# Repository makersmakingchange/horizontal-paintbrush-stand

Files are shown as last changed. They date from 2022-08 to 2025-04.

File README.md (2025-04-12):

#  Horizontal Paintbrush Stand
This is a paintbrush stand designed for use by a Mouth Painter. The Horizontal Paintbrush Stand has a series of spaced horizontal slots to rest the brush during use and enable the painter to switch between brushes independently. The stand has a female 1/4"-20 UNC connection for mounting using commercially available camera mounting equipment.

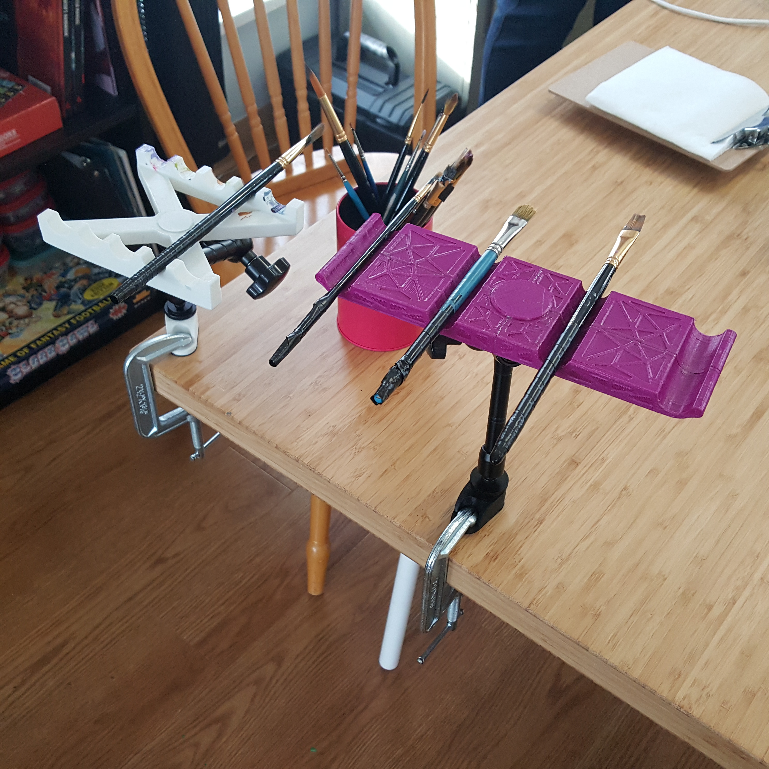
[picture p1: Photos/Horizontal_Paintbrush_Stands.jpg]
Picture of two Horizontal Paintbrush Stands. Each stand is mounted to a table using a Magic Arm, a C-Clamp mounting Adapter, and a C-Clamp.


## More info at
- [Makers Making Change Project Page](https://makersmakingchange.com/project/horizontal-paintbrush-stand/)

## How to Obtain a Horiztonal Horizontal Paintbrush Stand

### 1. Do it Yourself (DIY) or Do it Together (DIT)

This is an open-source assistive technology, so anyone is free to build it. All of the files and instructions required to build the Horizontal Paintbrush Stand are contained within this repository. Refer to the Maker Guide below.

### 2. Request a build of this device

To get matched up with a volunteer maker to build the device, you can submit a build request through the [MMC Library Page](https://makersmakingchange.com/project/horizontal-paintbrush-stand/). As the requestor, you will be responsible for the cost of materials and any shipping.

### 3. How to build this device for someone else

If you have the skills and equipment to build a device like this and would like to donate your time to create the switch for someone who needs it, visit the [MMC Maker Wanted](https://makersmakingchange.com/maker-wanted/) section to get in touch with a user.

## Files
### Documentation
| Document             | Version | Link |
|----------------------|---------|------|
| Design Rationale     | 1.0     | [Horizontal_Paintbrush_Stand_Design_Rationale](/Documentation/Horizontal_Paintbrush_Stand_Design_Rationale_v1.0.pdf)|
| Maker Guide          | 1.0     | [Horizontal_Paintbrush_Stand_Maker_Guide](/Documentation/Horizontal_Paintbrush_Stand_Maker_Guide_v1.0.pdf)          |
| Bill of Materials    | 1.0     | [Horizontal_Paintbrush_Stand_Bill_of_Materials](/Documentation/Horizontal_Paintbrush_Stand_BOM_v1.0.xlsx)           |
| User Guide           | 1.0     | [Horizontal_Paintbrush_Stand_User_Guide](/Documentation/Horizontal_Paintbrush_Stand_User_Guide_v1.0.pdf)            |
| Changelog            | 1.0     | [Horizontal_Paintbrush_Stand_Changelog](/Documentation/Horizontal_Paintbrush_Stand_ChangeLog_v1.0.pdf)              |

### Design Files
[CAD Files](/Design_Files)

### Build Files
 - [3D Printing Files](/Build_Files/3D_Printing)

## Attribution
Designed by Jake McIvor (Makers Making Change) in consultation with artist Kaileen Selig.

## License
Everything needed or used to design, make, test, or prepare the Horizontal Paintbrush Stand is licensed under the CERN 2.0 Permissive license <https://ohwr.org/project/cernohl/wikis/Documents/CERN-OHL-version-2> (CERN-OHL-P) . 

Accompanying material such as instruction manuals, videos, and other copyrightable works that are useful but not necessary to design, make, test, or prepare the Horizontal Paintbrush Stand are published under a Creative Commons Attribution-ShareAlike 4.0 license <https://creativecommons.org/licenses/by-sa/4.0/> (CC BY-SA 4.0).

<!-- ABOUT MMC START -->
## About Makers Making Change
[Makers Making Change Logo](https://www.makersmakingchange.com/)

Makers Making Change is a program of [Neil Squire](https://www.neilsquire.ca/), a Canadian non-profit that uses technology, knowledge, and passion to empower people with disabilities.

Makers Making Change leverages the capacity of community based Makers, Disability Professionals and Volunteers to develop and deliver affordable Open Source Assistive Technologies.

 - Website: [www.MakersMakingChange.com](https://www.makersmakingchange.com/)
 - GitHub: [makersmakingchange](https://github.com/makersmakingchange)
 - Bluesky: [@makersmakingchange.bsky.social](https://bsky.app/profile/makersmakingchange.bsky.social)
 - Instagram: [@makersmakingchange](https://www.instagram.com/makersmakingchange)
 - Facebook: [makersmakechange](https://www.facebook.com/makersmakechange)
 - LinkedIn: [Neil Squire Society](https://www.linkedin.com/company/neil-squire-society/)
 - Thingiverse: [makersmakingchange](https://www.thingiverse.com/makersmakingchange/about)
 - Printables: [MakersMakingChange](https://www.printables.com/@MakersMakingChange)

### Contact Us
For technical questions, to get involved, or to share your experience we encourage you to [visit our website](https://www.makersmakingchange.com/) or [contact us](https://www.makersmakingchange.com/s/contact).
<!-- ABOUT MMC END -->

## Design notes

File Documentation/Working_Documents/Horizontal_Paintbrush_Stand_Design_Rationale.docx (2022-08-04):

# Introduction

This project was originated in consultation with a mouth painter who was looking for a way to independently swap paintbrushes and temporarily but them down to rest. At the time, they were relying on a care aid to initially position the brush so they could grip it in their mouth with their lips and teeth.

# Research

Initial research did not uncover any suitable commercial or pre-existing DIY options. Most commercial options are intended to keep the brush in a vertical position, and do not provide easy access to the handle.

A more recent search did yield a horizontal brush holder (e.g., https://genevafineart.com/collections/all-items/products/brush-holder, $120) but this is expensive and would be difficult to mount at the proper height.

# Requirements

## Goals

G01 | Provide a means for user to independently place down and swap between several paintbrushes.

## Functional Requirements

F01 | The stand must have space for a minimum of 4 brushes.
F02 | The stand must be mounted securely.
F03 | The stand must be easily repositionable to adjust for height.
F04 | The stand must enable user to put down a brush while gripping it with their mouth.
F05 | The stand must enable the user to retrieve a brush by gripping it with their mouth.
F06 | Brushes must be adequately spaced to provide clearance for ventilator.

## Non-functional Requirements

NF01 | Design must be maker-friendly.

## Constraints

C01 | Design must be released open-source.

# Detailed Design

## Brush Slot Spacing

A spacing of 60 mm between the brushes was found to be a good compromise between keeping the brushes close together and allowing enough room between them so they can be easily grasped without interfering with the ventilator. A painter that doesn't use a ventilator may be able to have the brushes spaced closer together.

## Number of Slots

The user requested to have access to at least 3-4 brushes.

## Slot Size

A semi-circular slot with a radius of 8 mm was chosen to accommodate most paint brush handles.

## Mounting

One of the most important functional requirements is that the brush stand is quick and easy to setup and can be adjusted to the right position. A 1/4"-20 UNC tee insert nut was selected as a cost-effective and maker-friendly method of adding a modular mounting connection point. This connection point can be used with a variety of commercially available camera mounting equipment, including an articulating arm, or “Magic Arm”.

The mounting configuration for the user was chosen based on the availability of magic arms from related projects, as well as the requirement to have a non-permanent connection to the working surface.

- 3D printed C-Clamp Adapter (i.e., https://makersmakingchange.com/project/c-clamp-threaded-adapter/)
- Off-the-shelf C-Clamp (e.g., https://www.homedepot.ca/product/bessey-bessey-2-1-2-inch-900-lb-drop-forged-c-clamp-with-1-3-8-inch-throat-depth/1000816966)
- Off-the-shelf Articulating Magic Arm (e.g., https://www.amazon.ca/Koolehaoda-Adjustable-Articulating-Compatible-Microphones/dp/B08PC21P2D)

# V0.1

The initial prototype of the design had five slots, spaced apart by 22 mm. Each slot was a semi-circular with a diameter of 16 mm. The brush is supported by two 10 mm wide sections separated by 90 mm center-to-center.

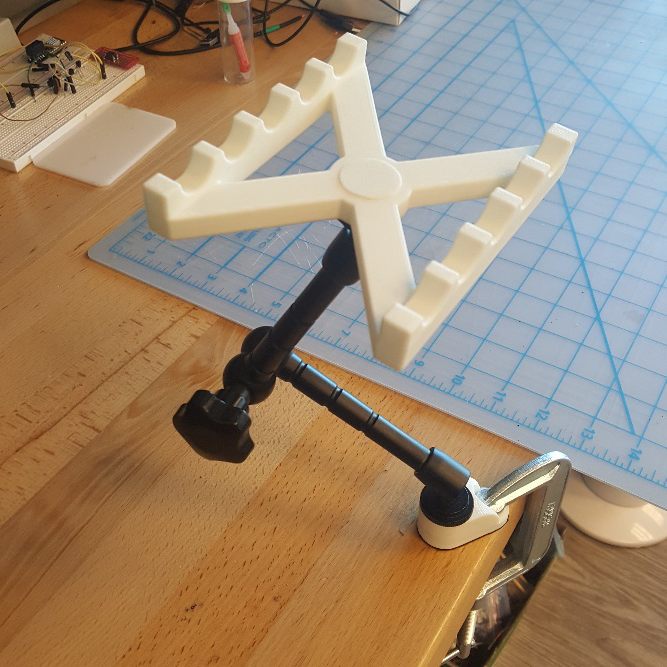
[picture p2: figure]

Figure 1: Initial Prototype

Assembly

The T-Nut is pressed into the stand from the top, and then the cap is glued into place.

# V0.2

Based on feedback from the user, the spacing between brushes was increased from 22 mm to 60 mm and the number of slots was reduced from five to four. Instead of two discrete supports the support was made continuous to make it easier to rest the brushes.

This version was also intended to be more aesthetically stylish.

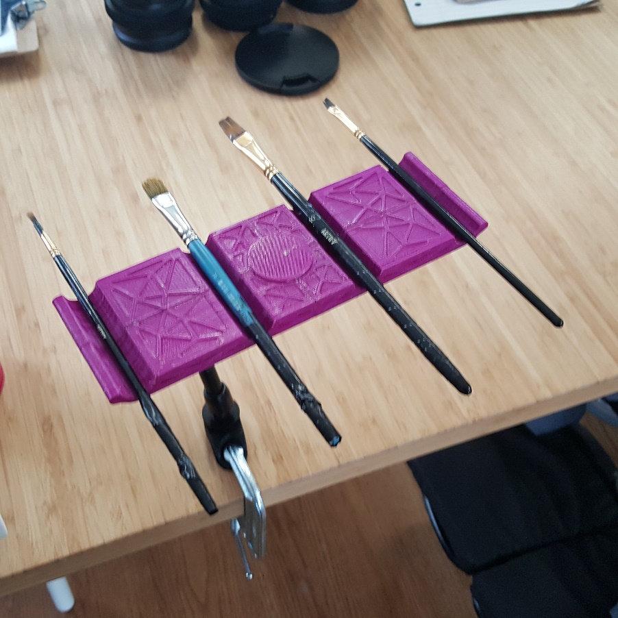
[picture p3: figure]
A picture of a 3d printed horizontal paintbrush stand. This is version 0.2, which features 4 slots.

Figure 2: Version 0.2

© 2022 by Neil Squire. This work is licensed under the CC BY SA 4.0 License: http://creativecommons.org/licenses/by-sa/4.0 Files available at https://makersmakingchange.com/project/horizontal-paintbrush-stand/ Page 1 of 1

V1.0 | JUNE 2022 Horizontal Paintbrush Stand Design Rationale

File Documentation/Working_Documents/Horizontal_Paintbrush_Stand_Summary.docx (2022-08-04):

# Title

Horizontal Paintbrush Stand

## Subtitle

An easily mountable stand for paintbrushes.

## Device Specifications

Build Time:

< 1hr

1-4 hr

5-10hr

>10hr

Cost:

$0 - $10

$11 - $25

$26 - $50

$51 - $100

$101 - $250

$250+

Stage: Recently Added

Skills: 3D Printing; Mechanics

Need: Agility / Dexterity

Disability: Mobility / Physical

Difficulty: Beginner

License: CC BY-SA

Usages: Recreation and Leisure

Type:

Designer: Makers Making Change

## Device Details

### Overview

This is a paintbrush stand designed for use by a Mouth Painter. The Horizontal Paintbrush Stand has a series of spaced horizontal slots to rest the brush during use and enable the painter to switch between brushes independently. The stand has a female 1/4"-20 UNC connection for mounting using commercially available camera mounting equipment.

### Usage

A suitable mounting solution is connected to the bottom of the stand and the working surface. The stand is then positioned at an appropriate height for the user. The user can place and remove brushes to and from the stand as necessary.

### Build Instructions

This build consists of 3D printable parts and some commercial off-the-shelf hardware. Refer to the Maker Guide for instructions on what parts to obtain, and how to print the parts. There are two design variants: A and B.

#### Skills Required

- 3D Printing
- Mechanical Assembly

#### Time Required

3D Printing Time: A: 3h14m / B: 9h45m

Assembly Time: 15 minutes

#### Tools

- ¼”-20 Hex Bolt
- Crescent wrench / pliers for inserting Tee-nut

#### Components

Variant A:

- 1X 3D Printed Base
- 1X 3D Printed Cap
- 1X ¼”-20 UNC Tee Nut

Variant B:

- 2X 3D Printed Base1
- 2X 3D Printed Base2
- 1X 3D Printed Nut Insert
- 1X 3D Printed Cap
- 6X 3D Printed Pins
- 1X ¼”-20 UNC Tee Nut

#### 3D Printing

Refer to the Maker Guide for 3D Printing instructions.

### Design

This device was designed using Autodesk Fusion 360. Original design files are available in the repository.

### Attribution

Designed by Jake McIvor (Makers Making Change) in consultation with Kaileen Selig.

© 2022 by Neil Squire. This work is licensed under the CC BY SA 4.0 License: http://creativecommons.org/licenses/by-sa/4.0 Files available at https://makersmakingchange.com/project/horizontal-paintbrush-stand/ Page 1 of 2

V1.0 | JUNE 2022 Horizontal Paintbrush Stand Summary

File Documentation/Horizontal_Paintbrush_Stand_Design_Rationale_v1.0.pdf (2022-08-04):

V1.0 | JUNE 2022

## Horizontal Paintbrush Stand

## DESIGN RATIONALE

© 2022 by Neil Squire. (https://neilsquire.ca/)
This work is licensed under the CC BY SA 4.0 License: http://creativecommons.org/licenses/by-sa/4.0
Files available at https://makersmakingchange.com/project/horizontal-paintbrush-stand/ | Page 1 of 4

### Introduction

This project was originated in consultation with a mouth painter who was looking for a way to independently swap paintbrushes and temporarily but them down to rest. At the time, they were relying on a care aid to initially position the brush so they could grip it in their mouth with their lips and teeth.

### Research

Initial research did not uncover any suitable commercial or pre-existing DIY options. Most commercial options are intended to keep the brush in a vertical position, and do not provide easy access to the handle.

A more recent search did yield a horizontal brush holder (e.g., https://genevafineart.com/collections/allitems/products/brush-holder, (https://genevafineart.com/collections/all-items/products/brush-holder) $120) but this is expensive and would be difficult to mount at the proper height.

### Requirements

### Goals

G01 Provide a means for user to independently place down and swap between several paintbrushes.

### Functional Requirements

F01 | The stand must have space for a minimum of 4 brushes.
F02 | The stand must be mounted securely.
F03 | The stand must be easily repositionable to adjust for height.
F04 | The stand must enable user to put down a brush while gripping it with their mouth.
F05 | The stand must enable the user to retrieve a brush by gripping it with their mouth.
F06 | Brushes must be adequately spaced to provide clearance for ventilator.

### Non-functional Requirements

NF01 Design must be maker-friendly.

### Constraints

C01 Design must be released open-source.

## DESIGN RATIONALE

Files available at https://makersmakingchange.com/project/horizontal-paintbrush-stand/ | Page 2 of 4

### Detailed Design

### Brush Slot Spacing

A spacing of 60 mm between the brushes was found to be a good compromise between keeping the brushes close together and allowing enough room between them so they can be easily grasped without interfering with the ventilator. A painter that doesn't use a ventilator may be able to have the brushes spaced closer together.

### Number of Slots

The user requested to have access to at least 3-4 brushes.

### Slot Size

A semi-circular slot with a radius of 8 mm was chosen to accommodate most paint brush handles.

### Mounting

One of the most important functional requirements is that the brush stand is quick and easy to setup and can be adjusted to the right position. A 1/4"-20 UNC tee insert nut was selected as a cost-effective and maker-friendly method of adding a modular mounting connection point. This connection point can be used with a variety of commercially available camera mounting equipment, including an articulating arm, or “Magic Arm”.

The mounting configuration for the user was chosen based on the availability of magic arms from related projects, as well as the requirement to have a non-permanent connection to the working surface.

- 3D printed C-Clamp Adapter (i.e., https://makersmakingchange.com/project/c-clamp-threadedadapter/) (https://makersmakingchange.com/project/c-clamp-threaded-adapter/)
- Off-the-shelf C-Clamp (e.g., https://www.homedepot.ca/product/bessey-bessey-2-1-2-inch-900-lbdrop-forged-c-clamp-with-1-3-8-inch-throat-depth/1000816966) (https://www.homedepot.ca/product/bessey-bessey-2-1-2-inch-900-lb-drop-forged-c-clamp-with-1-3-8-inch-throat-depth/1000816966)
- Off-the-shelf Articulating Magic Arm (e.g., https://www.amazon.ca/Koolehaoda-Adjustable-Articulating-Compatible-Microphones/dp/B08PC21P2D) (https://www.amazon.ca/Koolehaoda-Adjustable-Articulating-Compatible-Microphones/dp/B08PC21P2D)

V0.1
The initial prototype of the design had five slots, spaced apart by 22 mm. Each slot was a semi-circular with a diameter of 16 mm. The brush is supported by two 10 mm wide sections separated by 90 mm center-to-center.

## DESIGN RATIONALE

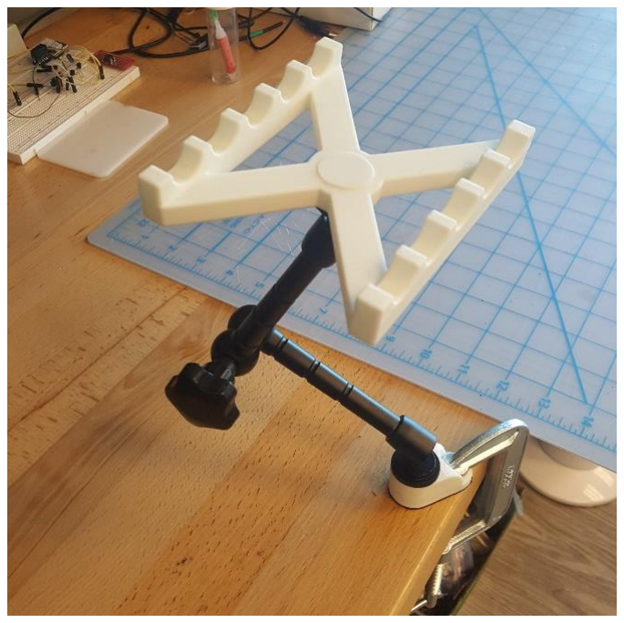
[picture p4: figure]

Files available at https://makersmakingchange.com/project/horizontal-paintbrush-stand/ | Page 3 of 4

Figure 1: Initial Prototype

Assembly

The T-Nut is pressed into the stand from the top, and then the cap is glued into place.

V0.2
Based on feedback from the user, the spacing between brushes was increased from 22 mm to 60 mm and the number of slots was reduced from five to four. Instead of two discrete supports the support was made continuous to make it easier to rest the brushes.

## DESIGN RATIONALE

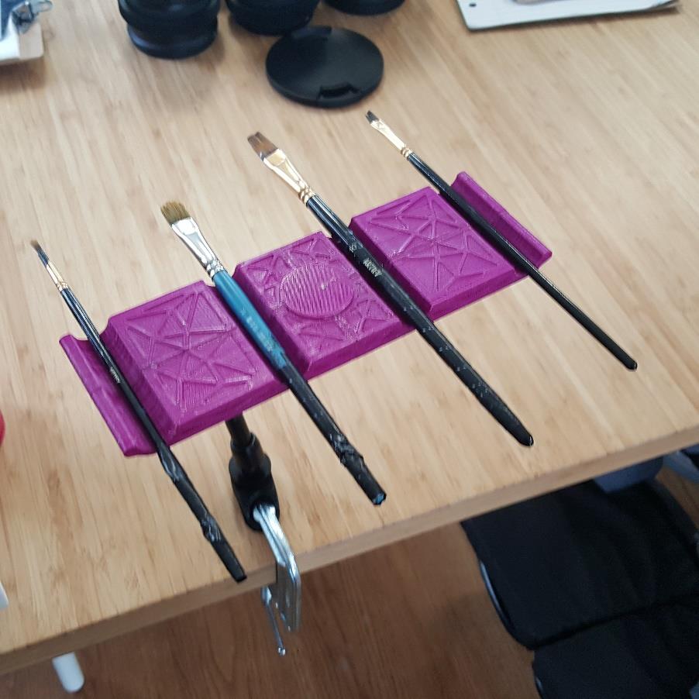
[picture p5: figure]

Files available at https://makersmakingchange.com/project/horizontal-paintbrush-stand/ | Page 4 of 4

This version was also intended to be more aesthetically stylish.

Figure 2: Version 0.2

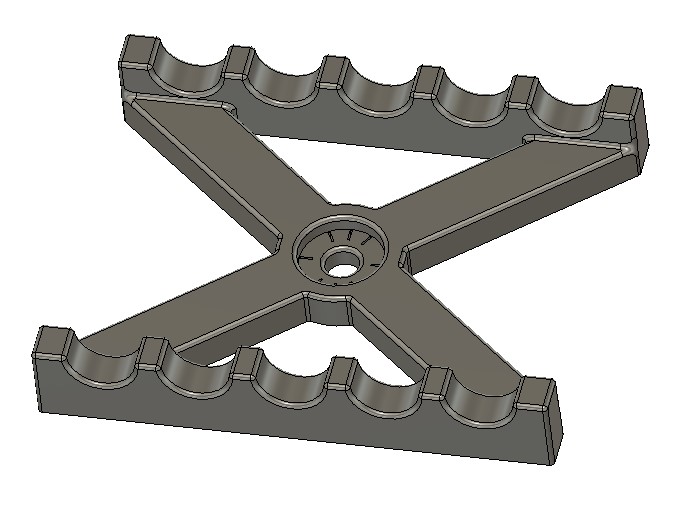
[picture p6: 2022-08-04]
Documentation/Working_Documents/Photos/Initial_Prototype.jpg

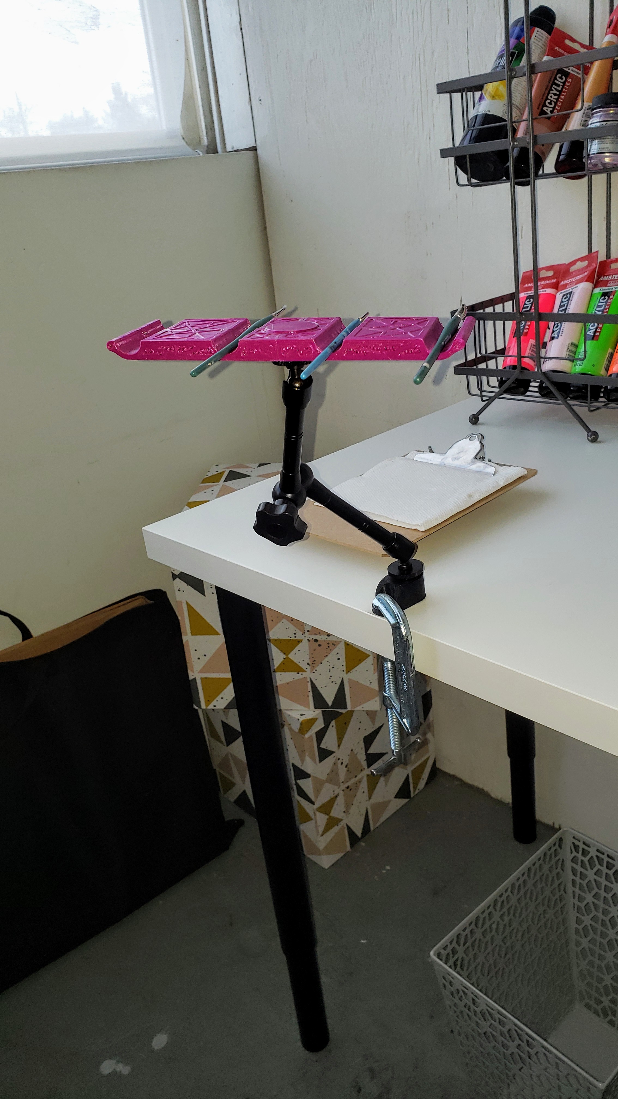
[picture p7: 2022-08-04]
Photos/V0.2/paintbrush stand.jpg

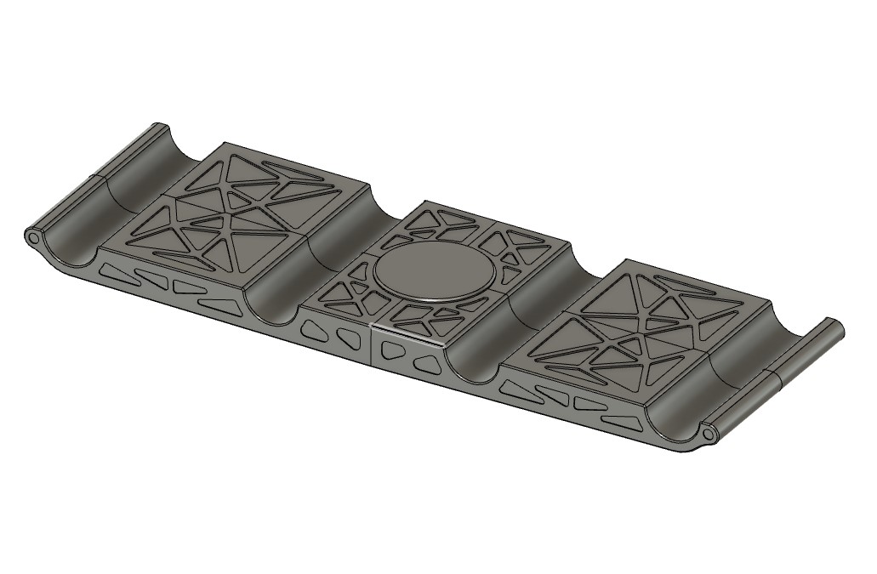
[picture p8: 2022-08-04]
Photos/V0.2/PaintBrushStand_v2.jpg

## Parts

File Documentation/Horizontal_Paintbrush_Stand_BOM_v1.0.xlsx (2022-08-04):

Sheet: BOM-A
Paintbrush Stand |  | Total Cost | Total Print time (hr) | Total filament (g)
Version: Variant A | Last Updated: 2022-Jul-06 | $1.55 | 3.25 | 43
Commercial Parts:
 | Part Name | QTY | Pkg QTY | PKG Price | Price per Unit | Price for qty needed | Link
Mechanical | 1/4"-20 UNC Tee Nut | 1 | 1 | $0.48 | $0.48 | $0.48 | https://www.homedepot.ca/product/paulin-1-4-inch-20-tee-nuts-4-prong-5-16-inch-barrel-length/1000129429
 |  | 0
 |  | 0
3D Printed Parts ESTIMATED PRICING USING 1KG ROLL COST: | $25.00
Part | Description | Quantity Needed | TOTAL Mass (g) | Estimated Price | Print Time (Min) |  | Link
A_Base |  |  | 42 | $1.05 | 192
A_Cap |  |  | 1 | $0.03 | 3
 |  |  |  | $0.00
 |  |  |  | $0.00
 |  |  |  | $0.00
 |  |  | Total Print Cost: | $1.07
Tools for Assembly
1/4"-20 Bolt
Alternatives (if there are other sources for some parts link them below)
Part and description | Link

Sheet: BOM-B
Paintbrush Stand |  | Total Cost | Total Print time (hr) | Total filament (g)
Version: Variant B | Last Updated: 2021-10-30 | #DIV/0! | 9.72 | 88
Commercial Parts:
Part type (Electrical. Mechanical, Sanitization, ect) | Part Name | Quantity Needed | Pkg Quantity | Price per package | Price per Unit | Price for qty needed | Link
Mechanical | 1/4"-20 UNC Tee Nut | 1 | 1 | $0.48 | $0.48 | $0.48 | https://www.homedepot.ca/product/paulin-1-4-inch-20-tee-nuts-4-prong-5-16-inch-barrel-length/1000129429
 |  |  |  |  | #DIV/0! | #DIV/0!
 |  |  |  |  | #DIV/0! | #DIV/0!
3D Printed Parts ESTIMATED PRICING USING 1KG ROLL COST: | $25.00
Part | Description | Quantity Needed | TOTAL Mass (g) | Estimated Price | Print Time (Min) |  | Link
B_Base 1 |  | 2 | 39 | $0.97 | 265
B_Base 2 |  | 2 | 39 | $0.97 | 265
B_Nut Insert |  | 1 | 6 | $0.15 | 35
B_Cap |  | 1 | 2 | $0.05 | 9
B_Pin |  | 6 | 2 | $0.05 | 9
 |  |  | Total Print Cost: | $2.20
Tools for Assembly
1/4"-20 Bolt
Alternatives (if there are other sources for some parts link them below)
Part and description | Link

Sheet: Mounting
 | Paintbrush Stand |  |  |  | Total Cost | Total Print time (hr) | Total filament (g)
 | Mounting |  |  |  | $0.00 | 0.00 | 0
ID | QTY | Description | Manufacturer Part Number | Manufacturer | Quantity Needed | Pkg Quantity | Price per Pkg | Price per Unit | Price for qty needed | Link
 |  | C-Clamp |  |  | 1 | 1 |  | $0.00 | $0.00
 |  | C-Clamp Camera Mount Adapter |  |  | 1 | 1 |  | $0.00 | $0.00

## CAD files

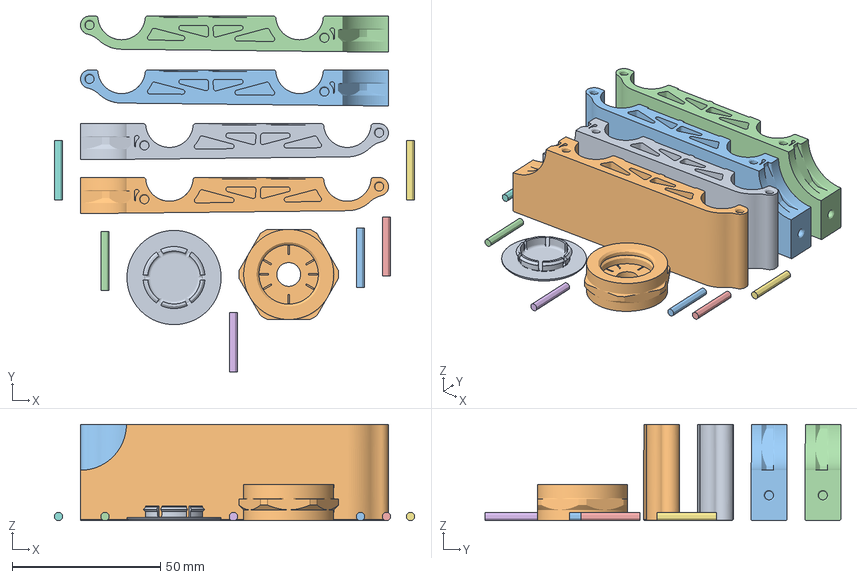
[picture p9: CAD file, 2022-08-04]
Build_Files/3D_Print_Files/Horizontal_Paintbrush_Stand_B.3mf
121.4 x 120.0 x 32.5 mm
Horizontal_Paintbrush_Stand_V0.2_Cap.stl
Horizontal_Paintbrush_Stand_V0.2_Nut_Insert.stl
Horizontal_Paintbrush_Stand_V0.2_Pin.stl
Horizontal_Paintbrush_Stand_V0.2_Stand_A.stl
Horizontal_Paintbrush_Stand_V0.2_Stand_B.stl

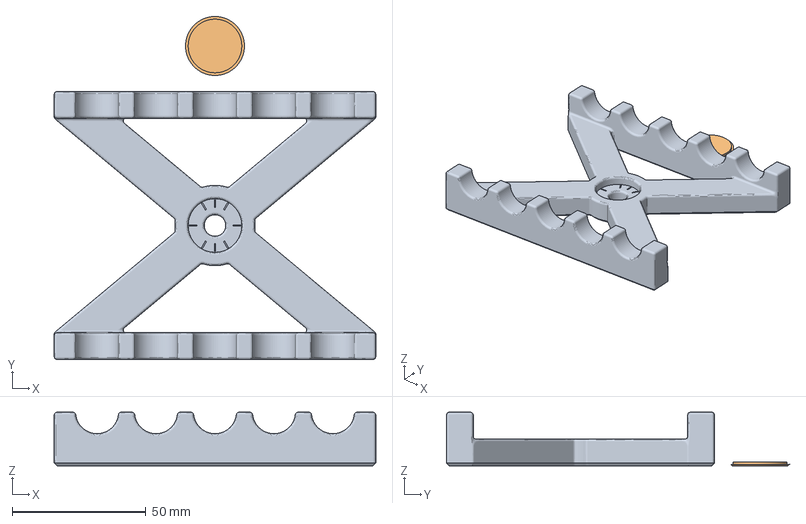
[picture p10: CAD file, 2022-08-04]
Build_Files/3D_Print_Files/Horizontal_Paintbrush_Stand_A.3mf
120.0 x 128.0 x 20.0 mm
Horizontal_Paintbrush_Stand_V0.1_Base.stl
Horizontal_Paintbrush_Stand_V0.1_Cap.stl

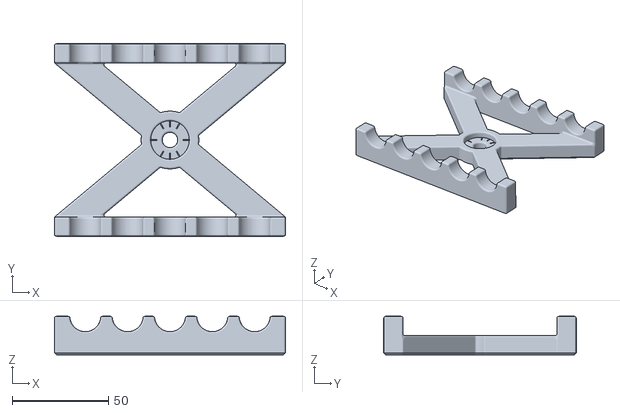
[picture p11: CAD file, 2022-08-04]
Build_Files/3D_Print_Files/Horizontal_Paintbrush_Stand_A_Base.stl
120.0 x 100.0 x 20.0

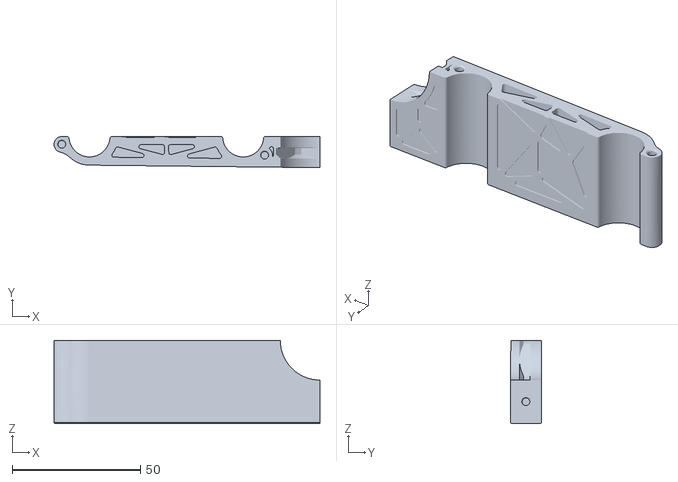
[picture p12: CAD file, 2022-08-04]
Build_Files/3D_Print_Files/Horizontal_Paintbrush_Stand_B_Base2.stl
103.9 x 12.1 x 32.5

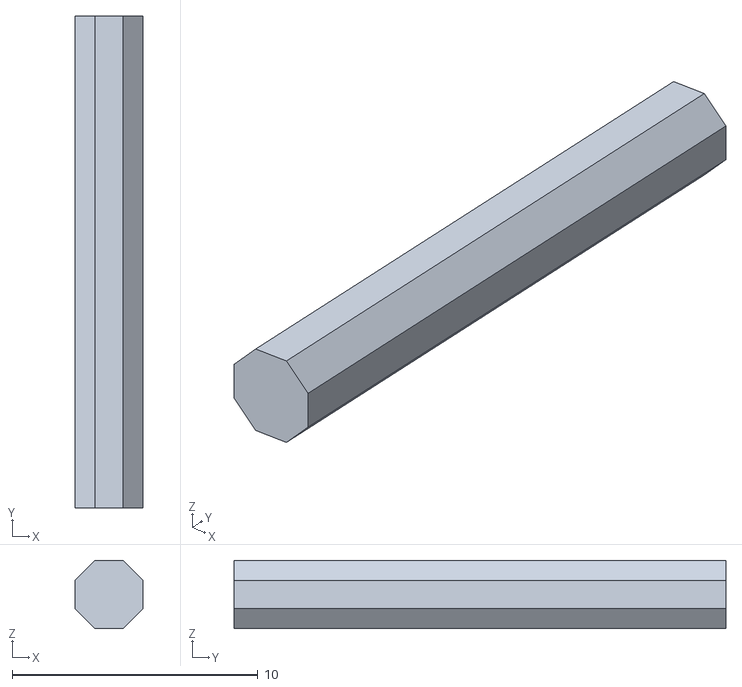
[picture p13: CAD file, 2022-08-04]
Build_Files/3D_Print_Files/Horizontal_Paintbrush_Stand_B_Pin.stl
2.77 x 20.0 x 2.77

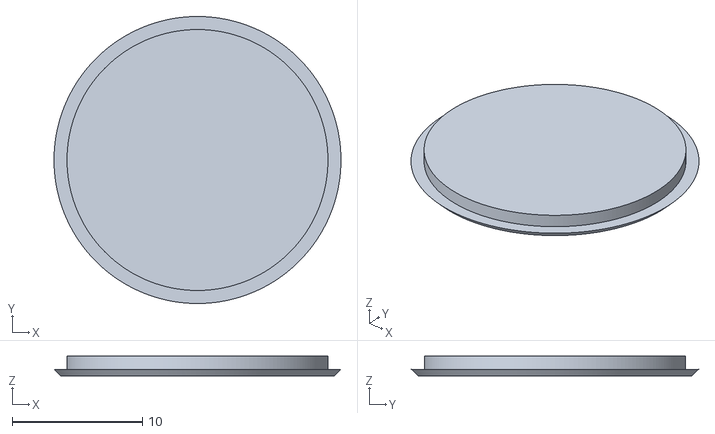
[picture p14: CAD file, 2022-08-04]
Build_Files/3D_Print_Files/Horizontal_Paintbrush_Stand_A_Cap.stl
22.0 x 22.0 x 1.50

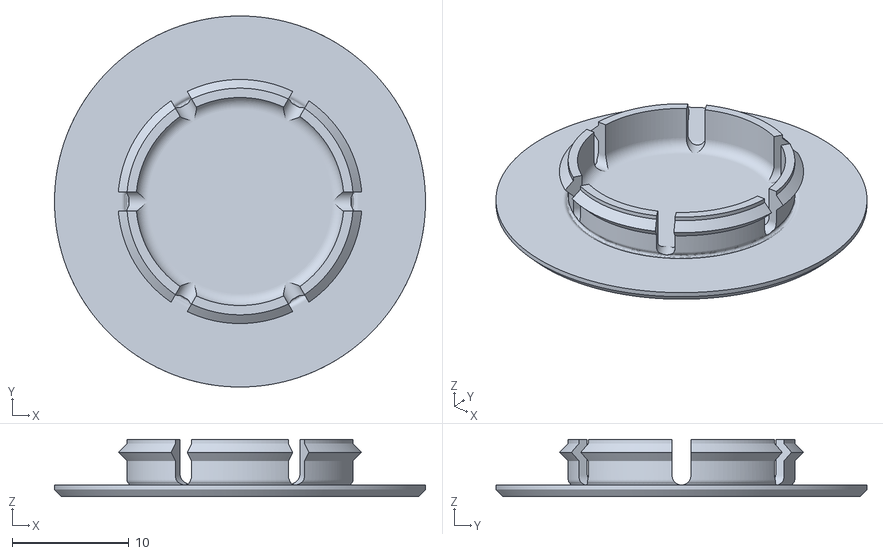
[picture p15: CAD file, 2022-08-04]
Build_Files/3D_Print_Files/Horizontal_Paintbrush_Stand_B_Cap.stl
31.8 x 31.8 x 4.90

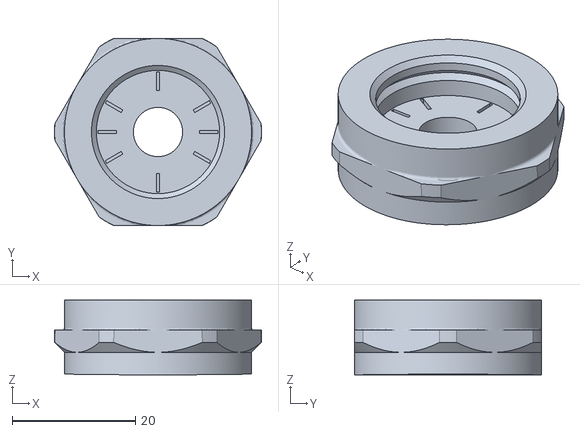
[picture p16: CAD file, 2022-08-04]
Build_Files/3D_Print_Files/Horizontal_Paintbrush_Stand_B_Nut_Insert.stl
33.6 x 30.4 x 12.1

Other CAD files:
Build_Files/3D_Print_Files/Horizontal_Paintbrush_Stand_B_Base1.stl
Design_Files/Horizontal_Paintbrush_Stand_v1.0.f3d

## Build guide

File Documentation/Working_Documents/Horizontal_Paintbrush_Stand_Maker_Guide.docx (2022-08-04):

# Overview

This document contains the necessary information to build the Horizontal Paintbrush Stand.

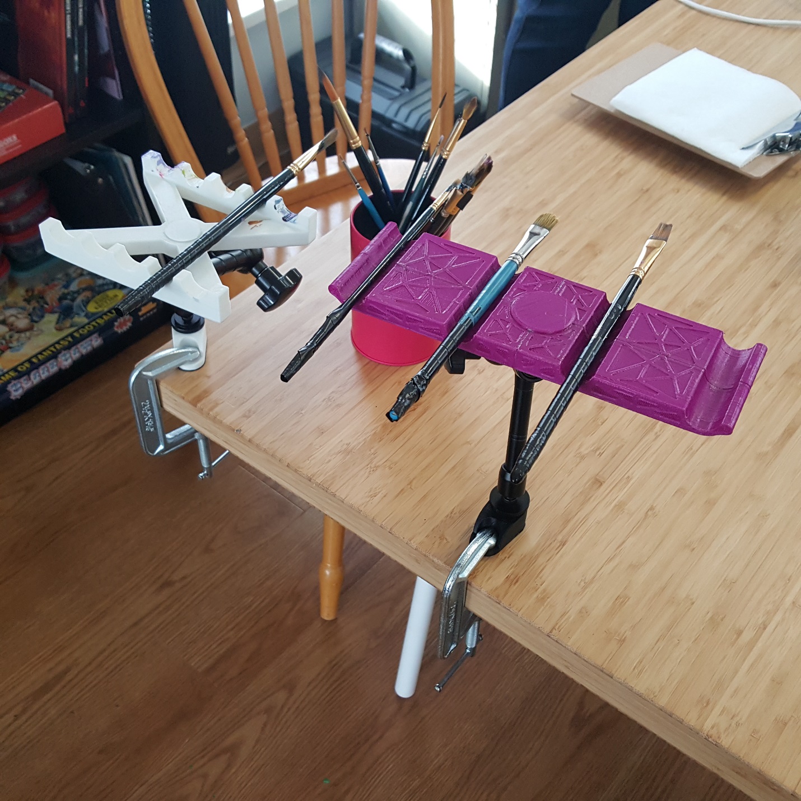
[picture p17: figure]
Picture of two Horizontal Paintbrush Stands. Each stand is mounted to a table using a Magic Arm, a C-Clamp mounting Adapter, and a C-Clamp.

Figure 1: Horizontal Paintbrush Stands. Variant A on the left, Variant B on the right. Show mounted with a magic arm, a C-Clamp, and a C-Clamp Adapter.

# Maker Checklist

This list provides an overview of the steps required to build and deliver the device to a user.

## Maker To Do List

- Read through the Maker Guide to become familiar with required components, tools, supplies, and safety gear and overall assembly steps.
- Talk to User about customization options
  - Variant A or B
  - Color
  - Number of brush slots
  - Brush slot spacing
  - Mounting Options
- Update Design if necessary
- Provide requestor with estimated cost of material and shipping.
- Order hardware components
- 3D Print components
- Gather tools, supplies, and safety equipment.
- Assemble the device
- Quality check the device
- Print “User Guide”

## Items to Give to User

- Assembled, tested brush stand
- “User Guide”

# Customization Guide

# 3D Printing Guide

## 3D Printing Summary

Metrics | Variant A | Variant B
Total Print Time (min) | 3h14m | 9h45m
Total Number of Components | 2 | 12
Typical Total Mass (g) | 42 | 85
Typical Number of Print Setups | 1 | 1

## 3D Printing Settings – Variant A

Print File Name | Qty | Total Print Time (hr:min) | Mass (g) | Infill (%) | Support(Y/N) | Layer Height/ Nozzle Diameter(mm) | Notes (orientation, special settings, etc.)
_A_Base.stl | 1 | 3h12m | 42 | 20 | N | 0.2/0.4
_A_Cap.st | 1 | 0h3m | 1 | 20 | N | 0.2/0.4

## 3D Printing Settings – Variant B

Print File Name | Qty | Total Print Time (hr:min) | Mass (g) | Infill (%) | Support(Y/N) | Layer Height/ Nozzle Diameter(mm) | Notes (orientation, special settings, etc.)
_B_Base1.stl | 2 | 4h25m | 39 | 20 | N | 0.2/0.4
_B_Base2.stl | 2 | 4h25m | 39 | 20 | N | 0.2/0.4
_B_Nut_Insert.stl | 1 | 0h35m | 6 | 20 | N | 0.2/0.4
_B_Cap.stl | 1 | 0h9m | 2 | 20 | N | 0.2/0.4
_B_Pin.stl | 6 | 0h9m | 2 | 20 | N | 0.2/0.4 | Better to print separate

## Post-Processing

- Remove any burrs. May be painted if desired.

# Assembly Guide – Variant A

## Required Components

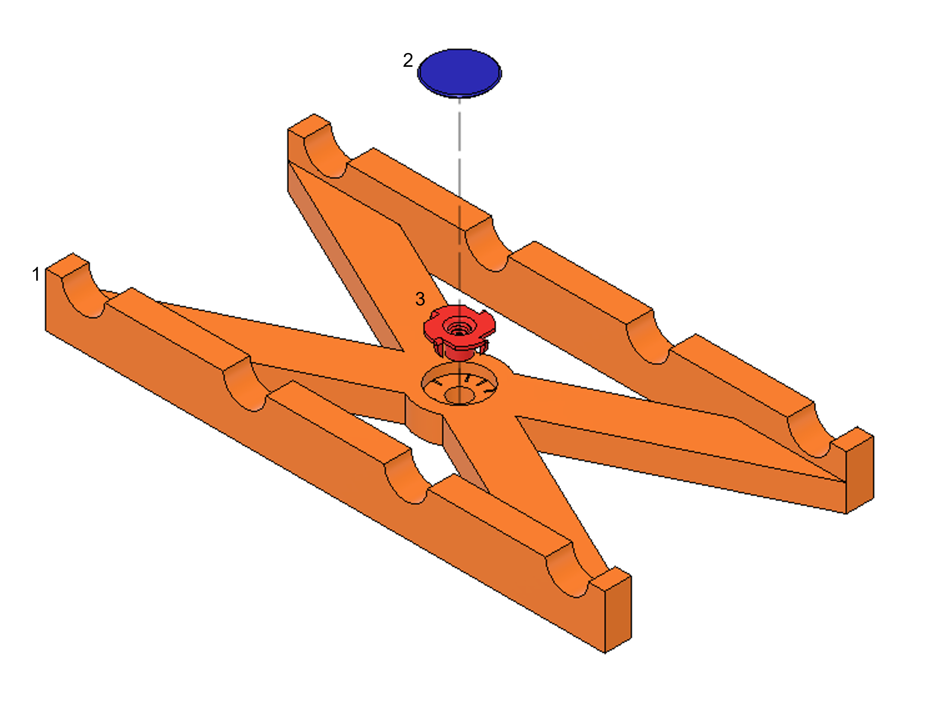
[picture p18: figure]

BOM

1. 3D Printed Base A
2. 3D Printed Cap A
3. ¼”-20 UNC Tee Nut Insert, 5/16” long

## Required Personal Protective Equipment (PPE)

- n/a

## Assembly Instructions – Variant A

### Step A.1

Insert the Tee Nut into the top of the Base. Use a ¼”-20 Washer and bolt to tighten and secure the Tee Nut into the Base. Nut Holder.

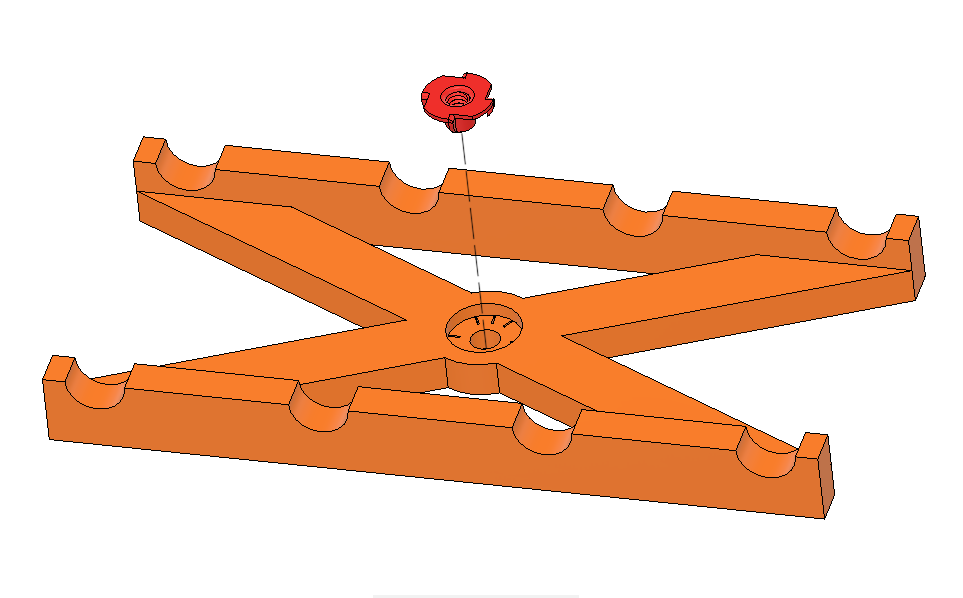
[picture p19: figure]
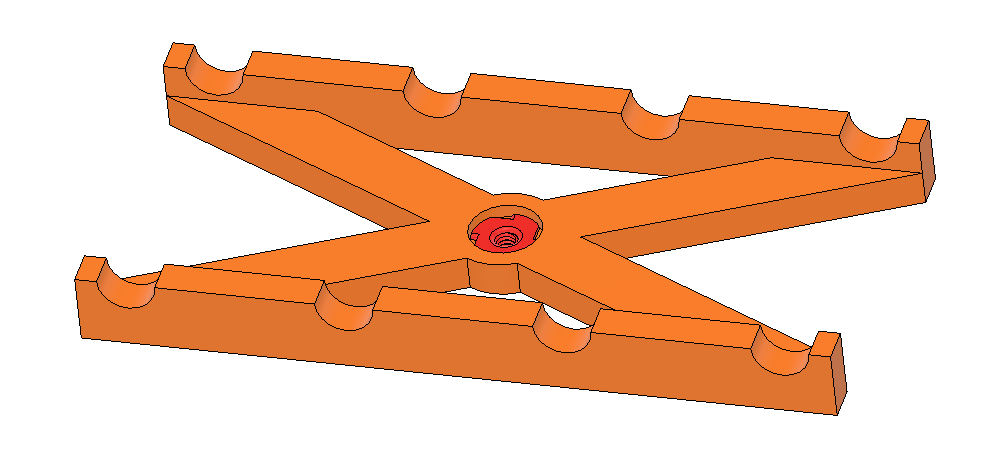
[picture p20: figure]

### Step A.2

Add the Cap to cover the Tee Nut.

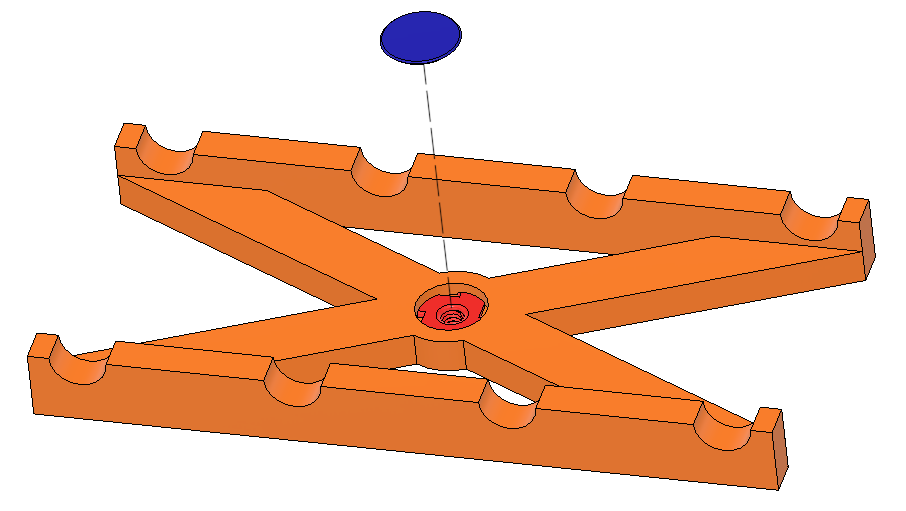
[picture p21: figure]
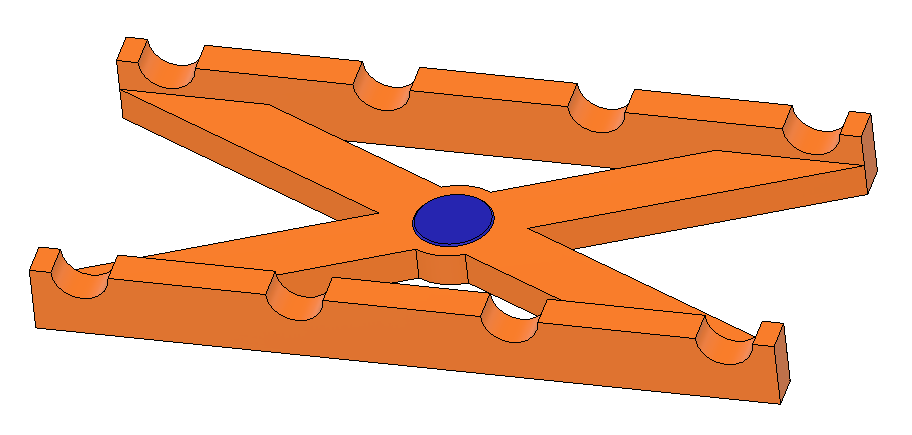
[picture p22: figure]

# Assembly Guide – Variant B

## Required Components

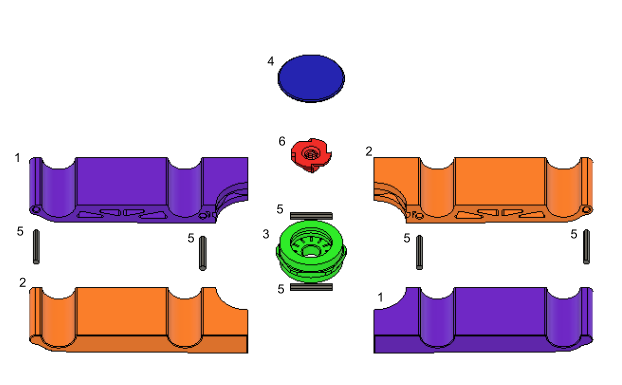
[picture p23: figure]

BOM

1. 2X Base B.1
2. 2X Base B.2
3. 1X Nut Insert
4. 1X Cap B
5. 6X Pins
6. 1X Tee Nut
7. Superglue

## Required Personal Protective Equipment (PPE)

- Eye protection (Superglue)
- Protective Gloves (Superglue)

## Assembly Instructions – Variant B

### Step B.1

Using 4 pins for alignment, use superglue to attach the sides of the bases together.

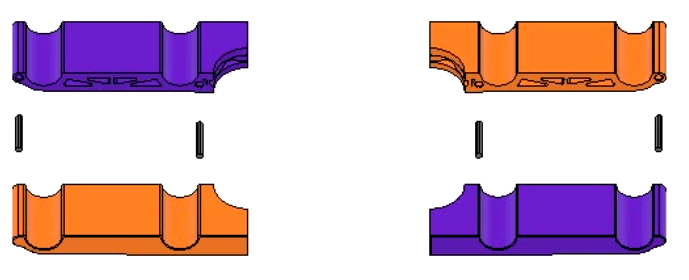
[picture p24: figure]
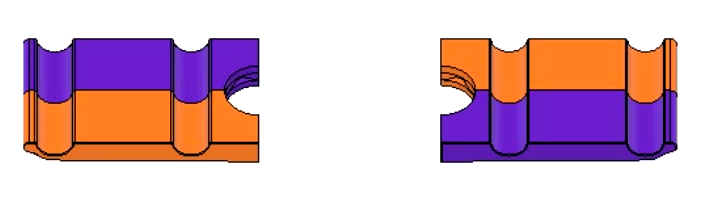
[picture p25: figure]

### Step B.2

Insert and glue the 2 remaining pins with the nut insert to secure the two halves.

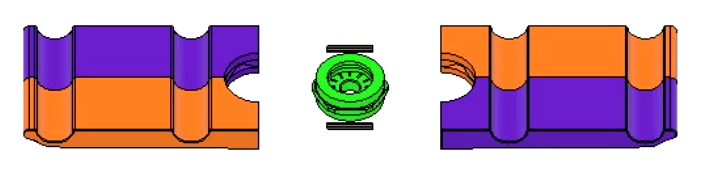
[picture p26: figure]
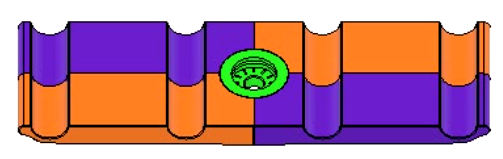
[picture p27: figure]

### Step B.3

Insert the Tee Nut from the top. Use a ¼”-20 Washer and bolt to tighten and secure the Tee Nut into the Nut Holder.

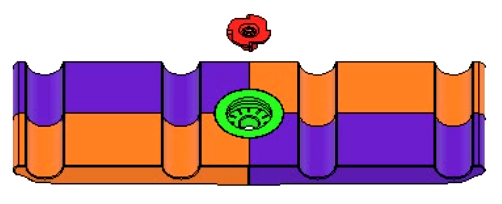
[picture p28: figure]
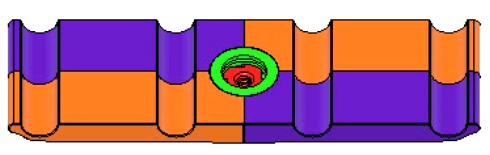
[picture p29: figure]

### Step B.4

Add the Cap to cover the Tee Nut.

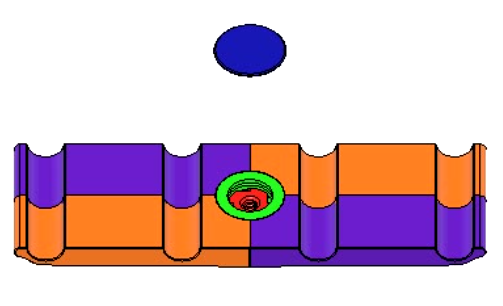
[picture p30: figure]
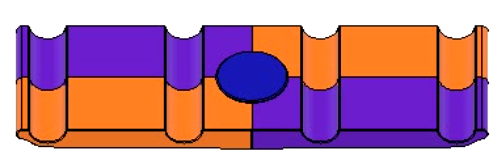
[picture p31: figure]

# Quality Check

1. Ensure the Tee Nut is installed correctly.
2. Check to make sure there are no sharp edges on the stand.

# Mounting Options

There Horizontal Brush Stand has a ¼”-20 UNC female thread on the bottom, so it is compatible with a variety of commercial and DIY mounting options.

## Magic Arm + C-Clamp

The Magic Arm / Articulating Arm provides a convenient way to adjust the position and orientation of the stand and can be locked in place with a single knob. Using the C-Clamp and C-Clamp Adapter is a cost-effect way of providing a sturdy, non-permanent connection to a table or other work surface. The size of the C-clamp can be chosen to accommodate different table thicknesses.

### Materials Required

Magic Arm

- https://www.amazon.ca/Koolehaoda-Adjustable-Articulating-Compatible-Microphones/dp/B08PC21P2D

C-Clamp

- https://www.homedepot.ca/product/bessey-2-1-2-inch-drop-forged-c-clamp-with-1-3-8-inch-throat-depth/1000816966

C-Clamp Adapter

- https://makersmakingchange.com/project/c-clamp-threaded-adapter/

### Instructions

1. Remove any unneeded hardware from the Magic Arm until just the male thread is left on both side.
2. Connect one side of the Magic Arm to the Paintbrush Stand. A locking washer or thread locker can be used to form a more reliable connection.
3. Connect the other end of the Magic Arm to the C-Clamp Adapter. A locking washer or thread locker can be used to form a more reliable connection.
4. Position the C-Clamp Adapter in an appropriate place on the work surface and use the C-clamp to clamp it in place. To provide better grip or protect the surface, a thin piece of rubber or DYCEM non-slip mat can be used.

## Loc-Line + C-Clamp

### Materials Required

1/2” Loc-Line Modular Hose (Enough segments to achieve desired length)

- https://www.bulkreefsupply.com/loc-line-modular-hose-segments.html (CAN)
- https://www.amazon.ca/Loc-Line-Coolant-Component-Copolymer-Segment/dp/B006R9ORIY (CAN)
- https://www.modularhose.com/ (USA)

1/2” Loc-Line Double Socket (SKU 90614)

- https://www.bulkreefsupply.com/loc-line-double-socket.html, SKU 202755 (CAN)
- https://www.modularhose.com/Loc-Line-90614 (USA)

1/2” Loc-Line Flat Surface/Fixed Mount

- https://www.amazon.ca/Loc-Line-Coolant-Component-Acetal-Copolymer/dp/B006T5JOV6 (CAN)
- https://www.modularhose.com/Loc-Line-51895?quantity=1&custcol_item_colors=8, SKU 51895-Blk (USA)

½” Loc-Line Modular Hose Assembly Pliers (Optional)

- https://www.modularhose.com/Loc-Line-60533?quantity=1&custcol_item_colors=8 (USA)1/2” Loc-Line Hose Assembly Pliers (Optional)
- https://www.amazon.ca/Loc-Line-78004-Hose-Assembly-Pliers/dp/B0025PUF1M (CAN)

¼”-20 UNC SHCS x

C-Clamp

- https://www.homedepot.ca/product/bessey-2-1-2-inch-drop-forged-c-clamp-with-1-3-8-inch-throat-depth/1000816966

C-Clamp Camera Mount Adapter

- https://makersmakingchange.com/project/c-clamp-threaded-adapter/

### Instructions

1. Attach the ½” Loc-Line Flat Surface/Fixed Mount to the bottom of the Horizontal Brush Stand using a ¼”-20 UNC screw and a ¼” lock washer.
2. Attach the ½” Loc-Line Double Socket to the ½” Loc-Line Flat Surface / Fixed Mount.
3. Attach the other ½” Loc-Line Flat Surface/Fixed Mount to a C-Clamp Camera Mount Adapter using a ¼”-20 UNC screw and a ¼” lock washer.
4. Determine how many ½”

© 2022 by Neil Squire. This work is licensed under the CC BY SA 4.0 License: http://creativecommons.org/licenses/by-sa/4.0 Files available at https://makersmakingchange.com/project/horizontal-paintbrush-stand/ Page 1 of 1

V1.0 | JUNE 2022 Horizontal Paintbrush Stand maker Guide

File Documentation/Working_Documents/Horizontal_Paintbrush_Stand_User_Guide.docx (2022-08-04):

## Introduction

The Horizontal Paintbrush Stand has a series of spaced horizontal slots to allow several paintbrushes to be rested and swapped between. The stand has a female 1/4"-20 UNC connection on the bottom so the stand can be mounted and adjustably positioned using commercially available camera mounting equipment.

## Features

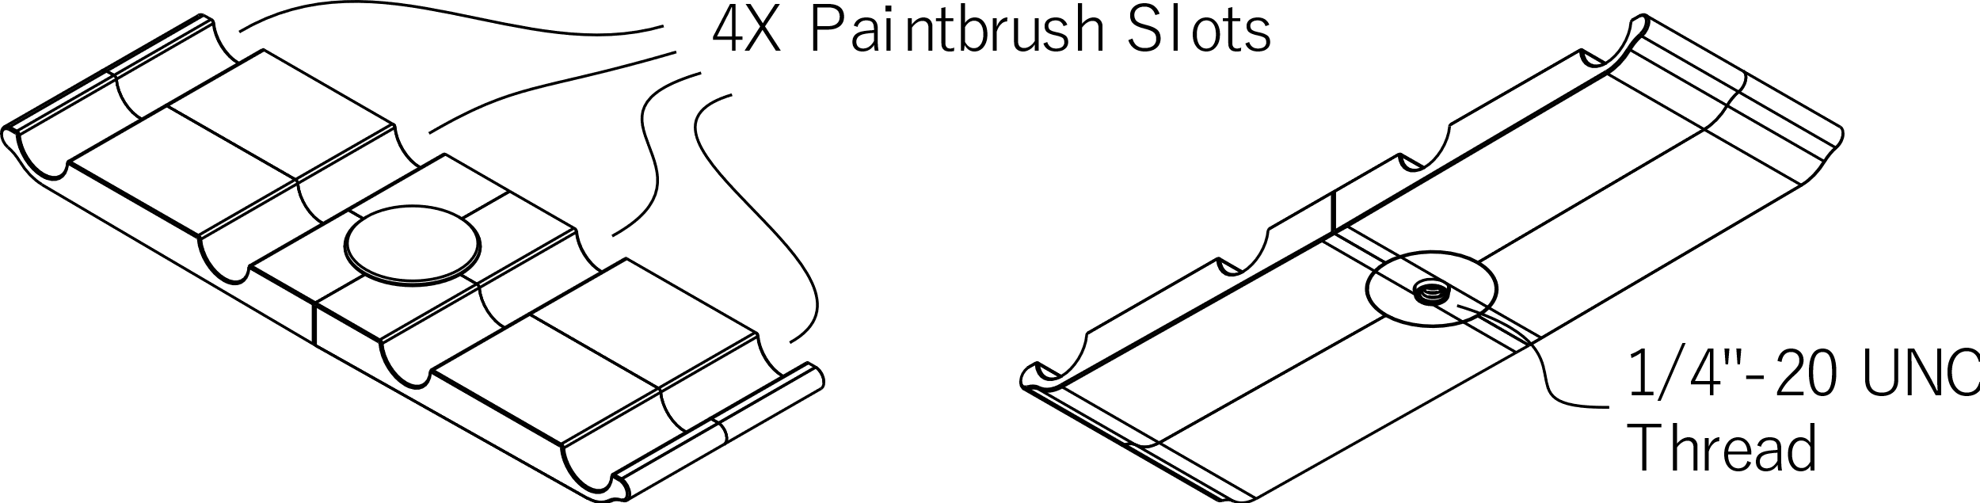
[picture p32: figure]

## Usage

Connect a compatible mounting solution to the threaded portion on the bottom of the stand and position it appropriately.

## Compatibility

This stand is compatible with a variety of commercial and DIY mounting systems that use a ¼”-20 thread, such as camera tripod mounts. For example, a magic arm and a 3d printed C-Clamp Adapter make an easily adjustable solution that can mount to a table.

## Specifications

- 208 mm Long x 65 mm Wide x 21 mm Deep
- 4 Brush Slots; 60 mm Spacing
- ¼”-20 UNC Mounting

## Cleaning

The stand can be wiped down with a damp cloth. Do not subject to high temperatures such as a dishwasher.

© 2022 by Neil Squire. This work is licensed under the CC BY SA 4.0 License: http://creativecommons.org/licenses/by-sa/4.0 Files available at https://makersmakingchange.com/project/horizontal-paintbrush-stand/ Page 2 of 3

V1.0 | JULY 2022 Horizontal Paintbrush Stand user Quick Guide

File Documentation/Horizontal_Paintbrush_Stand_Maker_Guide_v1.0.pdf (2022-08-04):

V1.0 | JUNE 2022

## Horizontal Paintbrush Stand

## MAKER GUIDE

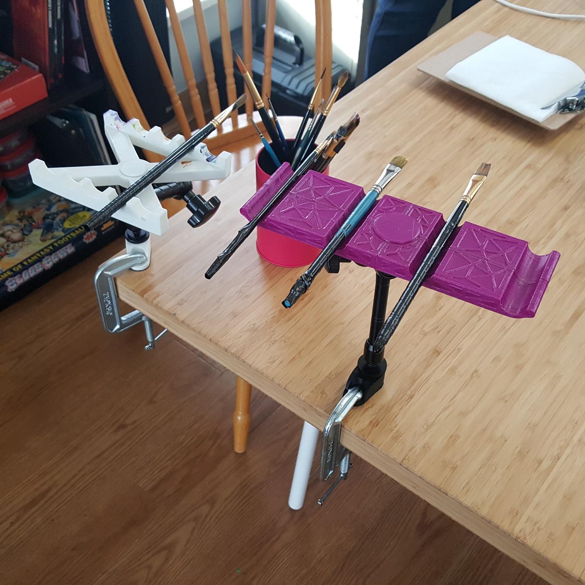
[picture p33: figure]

© 2022 by Neil Squire. (https://neilsquire.ca/)
This work is licensed under the CC BY SA 4.0 License: http://creativecommons.org/licenses/by-sa/4.0
Files available at https://makersmakingchange.com/project/horizontal-paintbrush-stand/ | Page 1 of 17

### Overview

This document contains the necessary information to build the Horizontal Paintbrush Stand.

Figure 1: Horizontal Paintbrush Stands. Variant A on the left, Variant B on the right. Show mounted with a magic arm, a C-Clamp, and a C-Clamp Adapter.

## MAKER GUIDE

Files available at https://makersmakingchange.com/project/horizontal-paintbrush-stand/ | Page 2 of 17

### Contents

Overview | 1
Maker Checklist | 4
Maker To Do List | 4
Items to Give to User | 4
Customization Guide | 5
3D Printing Guide | 6
3D Printing Summary | 6
3D Printing Settings – Variant A | 6
3D Printing Settings – Variant B | 6
Post-Processing | 6
Assembly Guide – Variant A | 7
Required Components | 7
Required Personal Protective Equipment (PPE) | 7
Assembly Instructions – Variant A | 8
Step A.1 | 8
Step A.2 | 9
Assembly Guide – Variant B | 10
Required Components | 10
Required Personal Protective Equipment (PPE) | 10
Assembly Instructions – Variant B | 11
Step B.1 | 11
Step B.2 | 11
Step B.3 | 12
Step B.4 | 13
Quality Check | 14
Mounting Options | 15
Magic Arm + C-Clamp | 15
Materials Required | 15
Instructions | 15

## MAKER GUIDE

Files available at https://makersmakingchange.com/project/horizontal-paintbrush-stand/ | Page 3 of 17
Loc-Line + C-Clamp | 16
Materials Required | 16
Instructions | 17

## MAKER GUIDE

Files available at https://makersmakingchange.com/project/horizontal-paintbrush-stand/ | Page 4 of 17

### Maker Checklist

This list provides an overview of the steps required to build and deliver the device to a user.

### Maker To Do List

Read through the Maker Guide to become familiar with required components, tools, supplies, and safety gear and overall assembly steps.
Talk to User about customization options
- Variant A or B
- Color
- Number of brush slots
- Brush slot spacing
- Mounting Options
Update Design if necessary
Provide requestor with estimated cost of material and shipping. Order hardware components
3D Print components
Gather tools, supplies, and safety equipment.
Assemble the device
Quality check the device
Print “User Guide”

### Items to Give to User

Assembled, tested brush stand “User Guide”

## MAKER GUIDE

Files available at https://makersmakingchange.com/project/horizontal-paintbrush-stand/ | Page 5 of 17

### Customization Guide

## MAKER GUIDE

Files available at https://makersmakingchange.com/project/horizontal-paintbrush-stand/ | Page 6 of 17

### 3D Printing Guide

### 3D Printing Summary

Metrics | Variant A | Variant B
Total Print Time (min) | 3h14m | 9h45m
Total Number of Components | 2 | 12
Typical Total Mass (g) | 42 | 85
Typical Number of Print Setups | 1 | 1

### 3D Printing Settings – Variant A

Print File Name | Qty | Total Print Time (hr:min) | Mass (g) | Infill (%) | Support(Y/N) | Layer Height/ Nozzle Diameter(mm) | Notes (orientation, special settings, etc.)
_A_Base.stl | 1 | 3h12m | 42 | 20 | N | 0.2/0.4
_A_Cap.st | 1 | 0h3m | 1 | 20 | N | 0.2/0.4

### 3D Printing Settings – Variant B

Print File Name | Qty | Total Print Time (hr:min) | Mass (g) | Infill (%) | Support(Y/N) | Layer Height/ Nozzle Diameter(mm) | Notes (orientation, special settings, etc.)
_B_Base1.stl | 2 | 4h25m | 39 | 20 | N | 0.2/0.4
_B_Base2.stl | 2 | 4h25m | 39 | 20 | N | 0.2/0.4
_B_Nut_Insert.stl | 1 | 0h35m | 6 | 20 | N | 0.2/0.4
_B_Cap.stl | 1 | 0h9m | 2 | 20 | N | 0.2/0.4
_B_Pin.stl | 6 | 0h9m | 2 | 20 | N | 0.2/0.4 | Better to print separate

### Post-Processing

- Remove any burrs. May be painted if desired.

## MAKER GUIDE

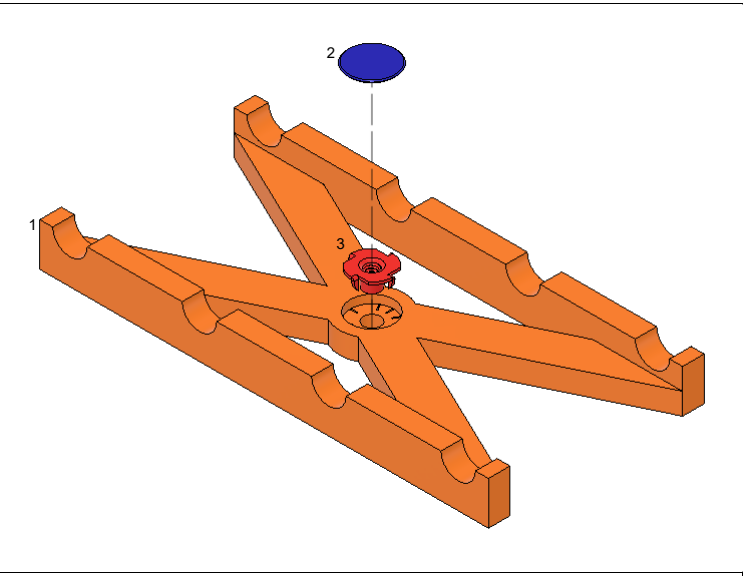
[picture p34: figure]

Files available at https://makersmakingchange.com/project/horizontal-paintbrush-stand/ | Page 7 of 17

### Assembly Guide – Variant A

### Required Components

BOM
1. 3D Printed Base A
2. 3D Printed Cap A
3. ¼”-20 UNC Tee Nut Insert, 5/16” long

### Required Personal Protective Equipment (PPE)

- n/a

## MAKER GUIDE

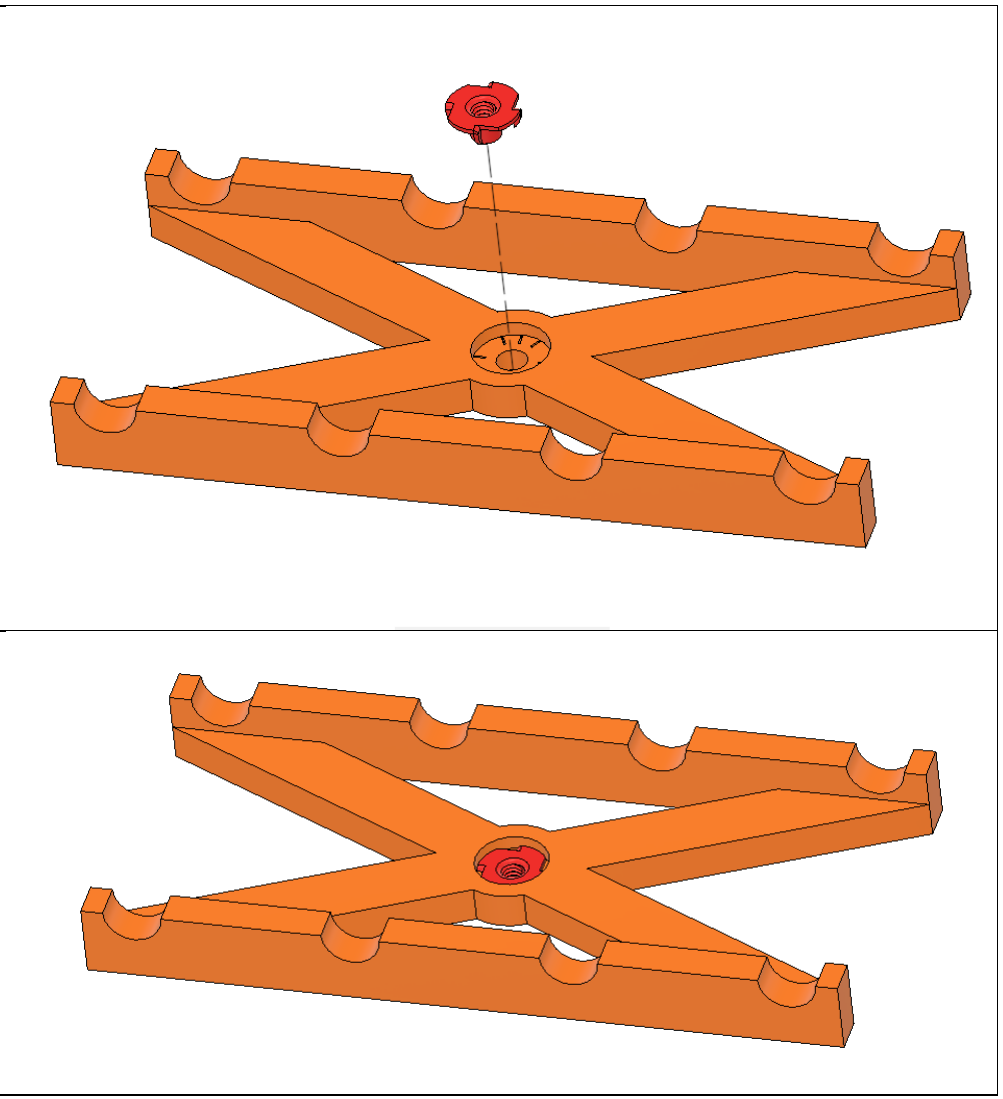
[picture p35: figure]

Files available at https://makersmakingchange.com/project/horizontal-paintbrush-stand/ | Page 8 of 17

### Assembly Instructions – Variant A

Step A.1
Insert the Tee Nut into the top of the Base. Use a ¼”-20 Washer and bolt to tighten and secure the Tee Nut into the Base. Nut Holder.

## MAKER GUIDE

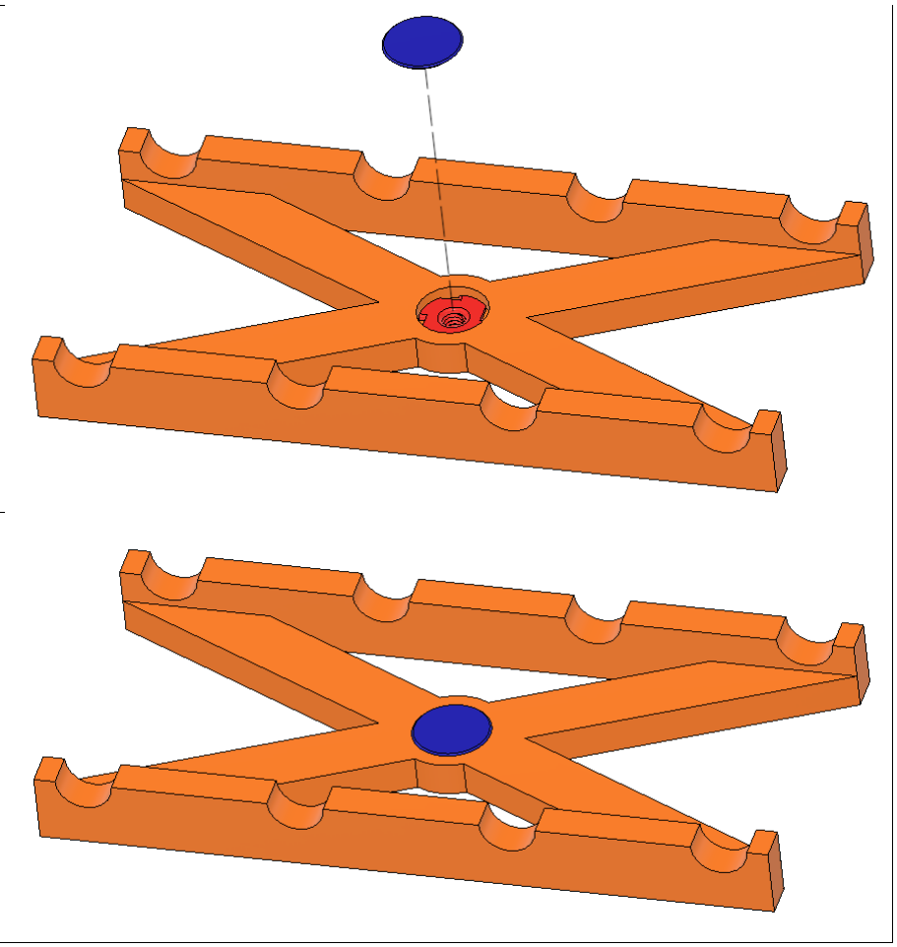
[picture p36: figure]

Files available at https://makersmakingchange.com/project/horizontal-paintbrush-stand/ | Page 9 of 17

Step A.2
Add the Cap to cover the Tee Nut.

## MAKER GUIDE

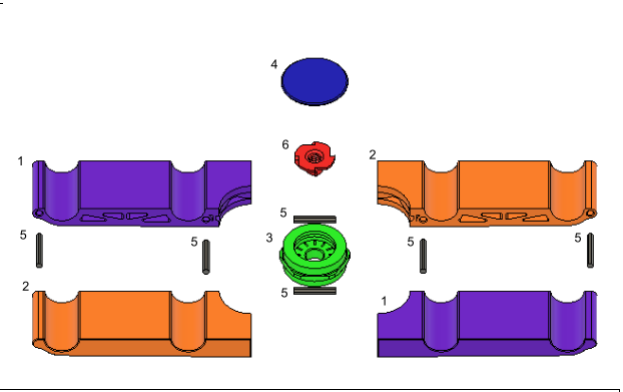
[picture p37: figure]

Files available at https://makersmakingchange.com/project/horizontal-paintbrush-stand/ | Page 10 of 17

### Assembly Guide – Variant B

### Required Components

BOM
1. 2X Base B.1
2. 2X Base B.2
3. 1X Nut Insert
4. 1X Cap B
5. 6X Pins
6. 1X Tee Nut
7. Superglue

### Required Personal Protective Equipment (PPE)

- Eye protection (Superglue)
- Protective Gloves (Superglue)

## MAKER GUIDE

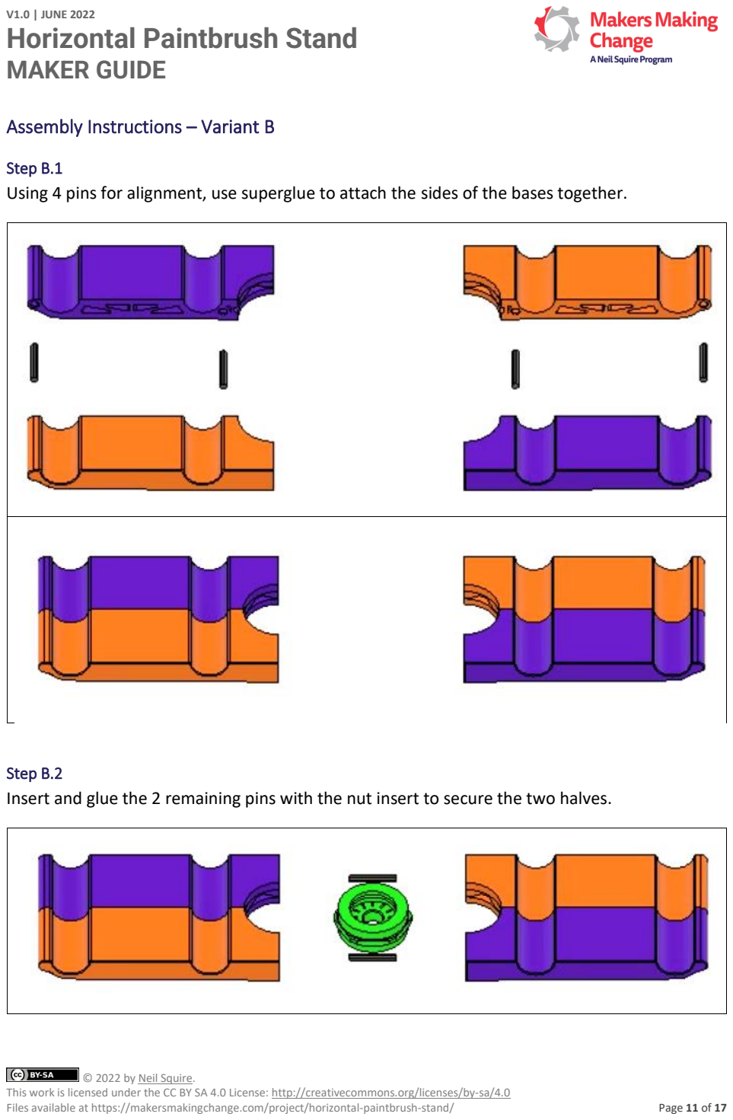
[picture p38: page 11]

Files available at https://makersmakingchange.com/project/horizontal-paintbrush-stand/ | Page 11 of 17

### Assembly Instructions – Variant B

Step B.1
Using 4 pins for alignment, use superglue to attach the sides of the bases together.

Step B.2
Insert and glue the 2 remaining pins with the nut insert to secure the two halves.

## MAKER GUIDE

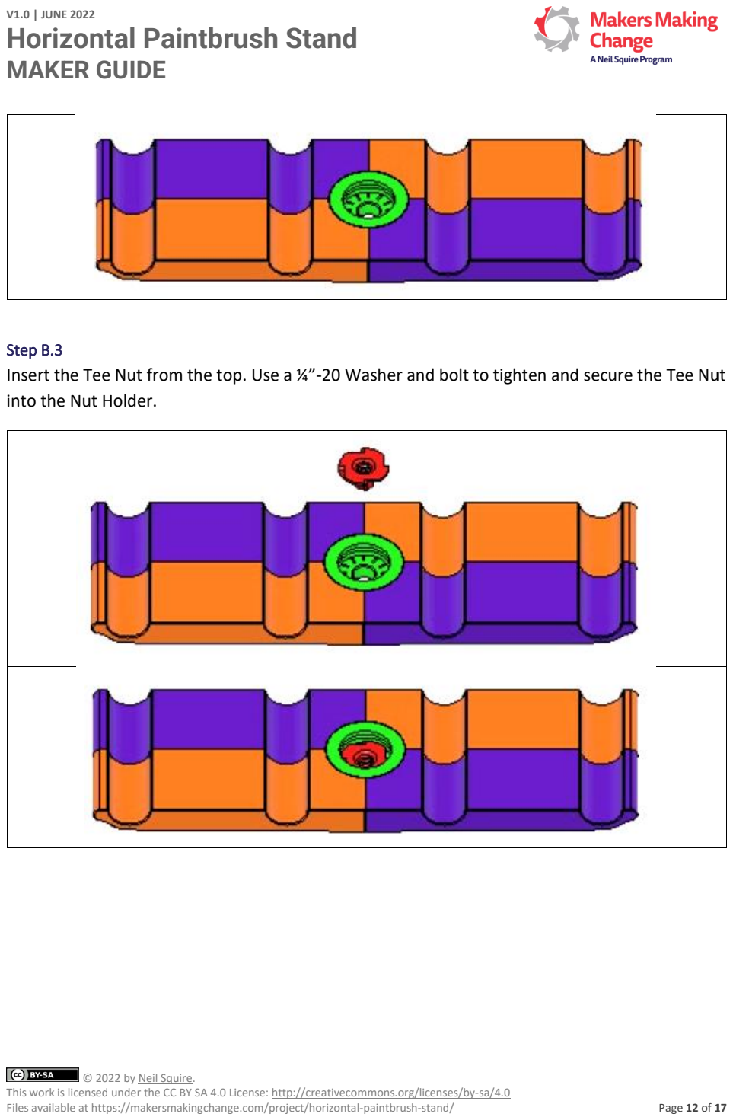
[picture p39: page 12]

Files available at https://makersmakingchange.com/project/horizontal-paintbrush-stand/ | Page 12 of 17

Step B.3
Insert the Tee Nut from the top. Use a ¼”-20 Washer and bolt to tighten and secure the Tee Nut into the Nut Holder.

## MAKER GUIDE

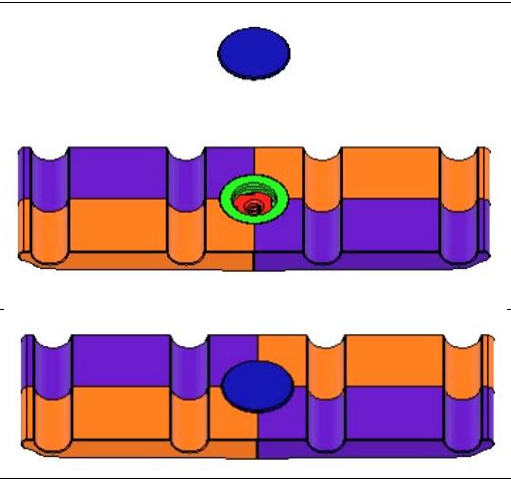
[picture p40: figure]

Files available at https://makersmakingchange.com/project/horizontal-paintbrush-stand/ | Page 13 of 17

Step B.4
Add the Cap to cover the Tee Nut.

## MAKER GUIDE

Files available at https://makersmakingchange.com/project/horizontal-paintbrush-stand/ | Page 14 of 17

### Quality Check

1. Ensure the Tee Nut is installed correctly.
2. Check to make sure there are no sharp edges on the stand.

## MAKER GUIDE

Files available at https://makersmakingchange.com/project/horizontal-paintbrush-stand/ | Page 15 of 17

### Mounting Options

There Horizontal Brush Stand has a ¼”-20 UNC female thread on the bottom, so it is compatible with a variety of commercial and DIY mounting options.

### Magic Arm + C-Clamp

The Magic Arm / Articulating Arm provides a convenient way to adjust the position and orientation of the stand and can be locked in place with a single knob. Using the C-Clamp and C-Clamp Adapter is a cost-effect way of providing a sturdy, non-permanent connection to a table or other work surface. The size of the C-clamp can be chosen to accommodate different table thicknesses.

Materials Required
Magic Arm
- https://www.amazon.ca/Koolehaoda-Adjustable-Articulating-Compatible-Microphones/dp/B08PC21P2D (https://www.amazon.ca/Koolehaoda-Adjustable-Articulating-Compatible-Microphones/dp/B08PC21P2D)

C-Clamp

- https://www.homedepot.ca/product/bessey-2-1-2-inch-drop-forged-c-clamp-with-1-3-8-inch-throat-depth/1000816966 (https://www.homedepot.ca/product/bessey-2-1-2-inch-drop-forged-c-clamp-with-1-3-8-inch-throat-depth/1000816966)
•

C-Clamp Adapter

- https://makersmakingchange.com/project/c-clamp-threaded-adapter/

Instructions
1. Remove any unneeded hardware from the Magic Arm until just the male thread is left on both side.
2. Connect one side of the Magic Arm to the Paintbrush Stand. A locking washer or thread locker can be used to form a more reliable connection.
3. Connect the other end of the Magic Arm to the C-Clamp Adapter. A locking washer or thread locker can be used to form a more reliable connection.
4. Position the C-Clamp Adapter in an appropriate place on the work surface and use the C-clamp to clamp it in place. To provide better grip or protect the surface, a thin piece of rubber or DYCEM non-slip mat can be used.

## MAKER GUIDE

Files available at https://makersmakingchange.com/project/horizontal-paintbrush-stand/ | Page 16 of 17

### Loc-Line + C-Clamp

Materials Required
1/2” Loc-Line Modular Hose (Enough segments to achieve desired length)
- https://www.bulkreefsupply.com/loc-line-modular-hose-segments.html (CAN)
- https://www.amazon.ca/Loc-Line-Coolant-Component-Copolymer-Segment/dp/B006R9ORIY (CAN)
- https://www.modularhose.com/ (USA)

1/2” Loc-Line Double Socket (SKU 90614)

- https://www.bulkreefsupply.com/loc-line-double-socket.html, SKU 202755 (CAN)
- https://www.modularhose.com/Loc-Line-90614 (USA)

1/2” Loc-Line Flat Surface/Fixed Mount

- https://www.amazon.ca/Loc-Line-Coolant-Component-Acetal-Copolymer/dp/B006T5JOV6 (CAN)
- https://www.modularhose.com/Loc-Line-51895?quantity=1&custcol_item_colors=8, SKU 51895-Blk (USA)

½” Loc-Line Modular Hose Assembly Pliers (Optional)

- https://www.modularhose.com/Loc-Line-60533?quantity=1&custcol_item_colors=8 (USA)1/2” Loc-Line Hose Assembly Pliers (Optional)
- https://www.amazon.ca/Loc-Line-78004-Hose-Assembly-Pliers/dp/B0025PUF1M (CAN)

¼”-20 UNC SHCS x

C-Clamp

- https://www.homedepot.ca/product/bessey-2-1-2-inch-drop-forged-c-clamp-with-1-3-8-inch-throat-depth/1000816966 (https://www.homedepot.ca/product/bessey-2-1-2-inch-drop-forged-c-clamp-with-1-3-8-inch-throat-depth/1000816966)
•

C-Clamp Camera Mount Adapter

## MAKER GUIDE

Files available at https://makersmakingchange.com/project/horizontal-paintbrush-stand/ | Page 17 of 17
- https://makersmakingchange.com/project/c-clamp-threaded-adapter/

Instructions

1. Attach the ½” Loc-Line Flat Surface/Fixed Mount to the bottom of the Horizontal Brush Stand using a ¼”-20 UNC screw and a ¼” lock washer.
2. Attach the ½” Loc-Line Double Socket to the ½” Loc-Line Flat Surface / Fixed Mount.
3. Attach the other ½” Loc-Line Flat Surface/Fixed Mount to a C-Clamp Camera Mount Adapter using a ¼”-20 UNC screw and a ¼” lock washer.
4. Determine how many ½”

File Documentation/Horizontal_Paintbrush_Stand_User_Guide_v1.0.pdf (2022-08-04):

V1.0 | JULY 2022

## Horizontal Paintbrush Stand

## USER QUICK GUIDE

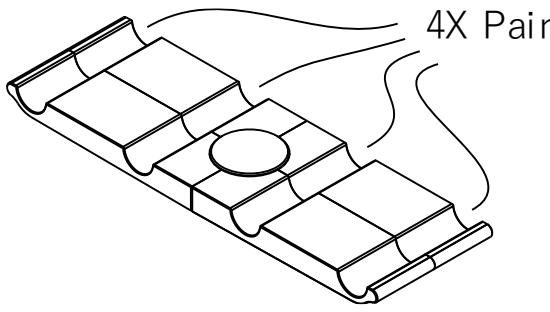
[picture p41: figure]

© 2022 by Neil Squire. (https://neilsquire.ca/)

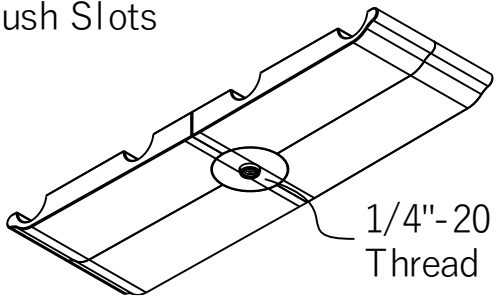
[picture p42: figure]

This work is licensed under the CC BY SA 4.0 License: http://creativecommons.org/licenses/by-sa/4.0
Files available at https://makersmakingchange.com/project/horizontal-paintbrush-stand/ | Page 1 of 1

### Introduction

The Horizontal Paintbrush Stand has a series of spaced horizontal slots to allow several paintbrushes to be rested and swapped between. The stand has a female 1/4"-20 UNC connection on the bottom so the stand can be mounted and adjustably positioned using commercially available camera mounting equipment.

### Features

### Usage

Connect a compatible mounting solution to the threaded portion on the bottom of the stand and position it appropriately.

### Compatibility

This stand is compatible with a variety of commercial and DIY mounting systems that use a ¼”-20 thread, such as camera tripod mounts. For example, a magic arm and a 3d printed C-Clamp Adapter make an easily adjustable solution that can mount to a table.

### Specifications

- 208 mm Long x 65 mm Wide x 21 mm Deep
- 4 Brush Slots; 60 mm Spacing
- ¼”-20 UNC Mounting

### Cleaning

The stand can be wiped down with a damp cloth. Do not subject to high temperatures such as a dishwasher.

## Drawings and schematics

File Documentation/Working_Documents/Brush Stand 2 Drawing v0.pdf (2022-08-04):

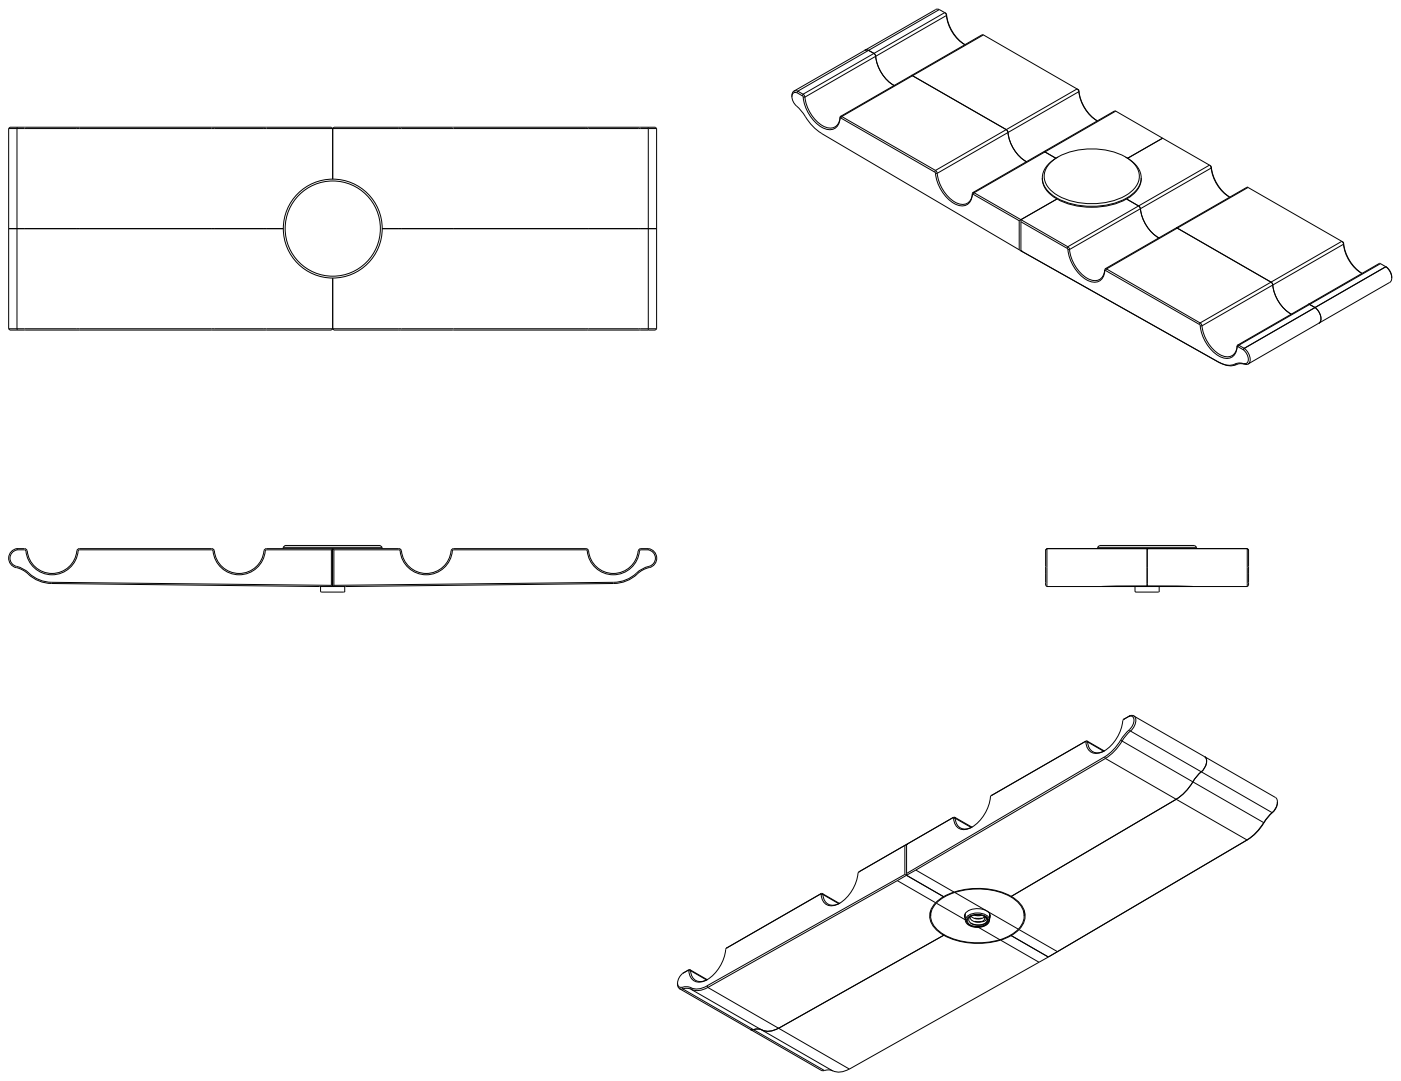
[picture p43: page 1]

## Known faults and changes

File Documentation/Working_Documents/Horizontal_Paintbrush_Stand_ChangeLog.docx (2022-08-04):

# Version 1.0 | Date 2022-July-04

Variant A:

Initial version. 5 slots spaced by 22 mm.

Variant B:

More solid, aesthetic design with 4 slots; 60 mm spacing.

© 2022 by Neil Squire. This work is licensed under the CC BY SA 4.0 License: http://creativecommons.org/licenses/by-sa/4.0 Files available at https://makersmakingchange.com/project/horizontal-paintbrush-stand/ Page 1 of 1

V1.0 | JULY 2022 Horizontal Paintbrush stand changelog
